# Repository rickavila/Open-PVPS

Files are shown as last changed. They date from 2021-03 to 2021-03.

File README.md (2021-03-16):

# Open-PVPS
Open Source Pandemic Virus Protection Systems

PVPS1 3 6-CADImage

Our goal is to develop open source pandemic virus protection technology that will significantly improve the safety of healthcare workers on the front lines of COVID-19.

To achieve this we are working to substantially reduce the manufacturing and operating cost of a PAPR (https://en.wikipedia.org/wiki/Powered_air-purifying_respirator) while maintaining HEPA filter efficiency (99.97% for 3um particles) with a design that can be easily mass produced anywhere in the world using standard commercial manufacturing machinery and automation. All work performed on this project is open source and freely available with a permissive open source license (CC BY-SA 4.0).

This repository contains a directory for "technical reports", a directory for CAD designs, and a directory for the electronics components. 

The technical reports directory contains documents that describe the technical work, calculations, and decisions that have been made for each major PAPR technical area. The major technical areas are:
* Overall PAPR System Specifications and Performance
* Face Shield, Visor, and Drape (coming soon)
* Power and Control Box
* Blower, Gauge, and Diffuser
* Filter

The CAD directory contains CAD files used to deveop the first PVPS prototypes. The file format is Autodesk Fusion 360. In the future we will also post STL files for anyone that would like to print out the 3D printed components.

The electronics directory contains files that define the physical circuit boards for the battery box and the program for the control board microprocessor. All of the electronics were designed by Jim Hannas with inputs from the team.

This project has a website at http://open-pvps.org

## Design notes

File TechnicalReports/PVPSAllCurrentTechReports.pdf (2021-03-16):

Tech note PVPS - S0001: – System Specifications and Perf | Author: Rick Avila : March 16, 2021

Pandemic Virus Protection Systems

1 | P a g e

Introduction

Similar to other professions involving hazardous environments, healthcare workers who come into contact with COVID-19 patients need equipment that provides high levels of airborne virus protection. Most healthcare institutions that treat COVID-19 patients use disposable N95 masks and plastic face shields which

(1) Do not fully protect the head and neck of the healthcare worker.
(2) Leave marks and bruises due to tight fitting straps around face and ears.
(3) Can be improperly worn without a tight seal.
(4) Can be difficult to breathe through after hours of use.
(5) Are expensive to replace every day for every healthcare worker.

A potential good solution to this problem is to provide each healthcare worker with a Powered Air-Purifying Respirator (PAPR). (https://en.wikipedia.org/wiki/Powered_air-purifying_respirator) However, the cost of commercially available PAPRs is extremely high ($1K to $2K/unit) and the availability is insufficient to support the estimated 18 million healthcare workers in the United States alone. What is needed is a safe and effective PAPR design that can be rapidly mass produced anywhere in the world with standard manufacturing equipment and can be made for as low a cost as possible.

This document outlines the high-level goals, specific technical specifications, and measured performance of the PVPS PAPR.

High Level Goals

- Safety
- Positive pressure keeps virus away from staff
- Quality replaceable air filter (HEPA) keeps breathing air clean
- Check for filter life with simple flow meter (Like commercial PAPR machines)
- Battery indicator allow staff to assure continuous blower function
- (New) Air exiting the PAPR must be filtered to prevent transmission from an infected healthcare worker using the device.
- Visibility
- Large replaceable visor for full viewing visibility
- Clear hood allows safety without isolation
- Comfort and Mobility
- Unit should be easy to wear while working for many hours
- Face shield provides easy doffing and donning
- No long hoses to keep track of
- Wide shroud makes it possible to operate stethoscope

Tech note PVPS - S0001: – System Specifications and Perf | Author: Rick Avila : March 16, 2021

Pandemic Virus Protection Systems

- Disinfection
- Throw away plastic curtain to facilitate easy cleanup
- Simple shape plastic shroud can be cleaned easily with spray and wipes
- Inside of shroud can be cleaned from one person to another easily
- Financial
- Cost must be < $400 for a new unit
- Operating cost must be less than the cost of using disposable respirators (N95 masks) and face shields.

Technical Specifications

- Airflow through filter and blower must be >= 6.0 CFM (169.9 L/min)
- Weight of entire unit must be < 40 ounces (1,133.98 grams)
- Noise level inside face shield must be <= 50 dBA
- Battery life with continuous use must be >= 6 hours
- Battery status must indicate amount of battery remaining
- HEPA filter replacement time must be >= 3 months
- Assigned Protection Factor must be >= 1,000
- Unit must operate for more than 2 years in a healthcare setting

Performance

We have conducted several performance evaluation tests including quantitative tests and healthcare provider evaluations. This section will be updated soon with the results of these tests.

Tech note PVPS - S0001: – System Specifications and Perf | Author: Rick Avila : March 16, 2021

Pandemic Virus Protection Systems

Revision History
Revision | Date | Who | Description
0 | 3/16/2021 | Rick Avila | Creation

Tech note PVPS - B0001: – Blower selection and Design Author: Bob Senzig : Sept 22 2020

Pandemic Virus Protection Systems

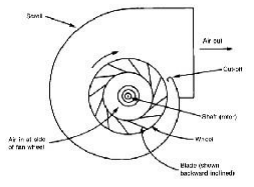
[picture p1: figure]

Blower Background

All commercial PAPR systems utilize a blower as part of the design. Blowers are capable of high flow and deliver a higher-pressure differential than a conventional fan. Our goal is to deliver between 3 and 10 CFM with good output pressure. On the drawing on the right you can see that this type of blower pulls from the inlet and discharge is a 90degree discharge using a centrifugal impeller

Blower Selection

Our final selection is shown here with an attached diffuser/deflector. It is a Foxconn 90mm Blower designed for small form factor Dell computers. It has the right CFM and adequate pressure output and is lightweight. It is a PVB120G12H-P01 J50GH-A00 J50GH 0J50GH 12V 0.75 4Wire Compatible for DELL OptiPlex 790 390 990 SFF CPU Fan Cooling
Fan. It is 146grams.
Initially we evaluated a 70mm blower but it did not provide the

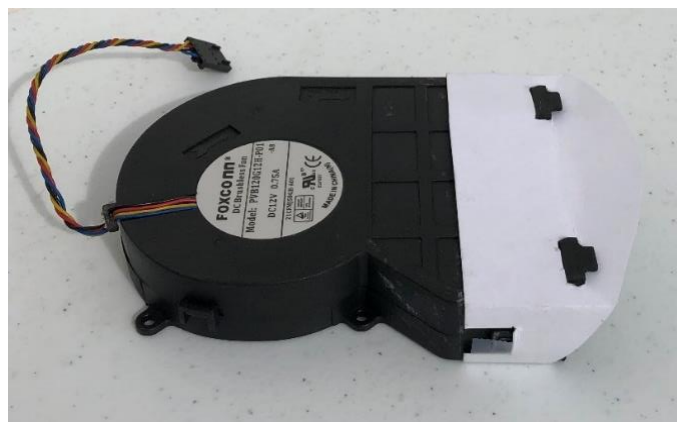
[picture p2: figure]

needed flow with our selected filter. The CFM for blowers are rated with no filter and it drops significantly when the filter is added to the inlet. For example: the GDStime blower is rated at 38CFM but we only saw 11 CFM at 12 volts with the Miller filter. We jumped to a GDSTIME 120mm blower to guarantee enough output. At the time we were using a Miller meter, that drastically underestimated the flow, to determine flow rate. Once we built a full prototype and experienced the impact of weight, we re-evaluated the priority on weight and moved to the smaller and lighter Foxconn 90mm blower. With a calibrated flow measurement, we were able to determine that perhaps a smaller fan could be used. The GDStime blower is 232grams.

Initial testing

Once a prototype was assembled using the 90mm Foxconn blower and Miller filter we conducted some stress tests wearing the mask. These tests were intended to see how the CO2
levels were maintained when doing a strenuous activity. These are not
substitutes for a more clinical environment test but were intended to
give an early indication of any issues. The CO2 levels in the front of the mask were periodically monitored using a Using a CO2 ppm meter periodically during the activity. it was determined that the airflow needed to be focused toward the front of the mask to reduce the CO2

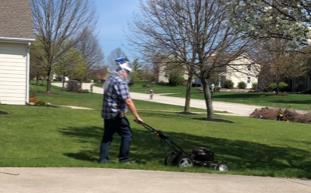
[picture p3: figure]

levels during exertion. A small Diffuser/Defector attached to the output of the blower improved airflow to the front of the mask and reduced the CO2 levels.
https://www.ebay.com/itm/Carbon-Dioxide-Meter-CO2-Detector-Indoor-Air-Quality-RH-Meter-0-2000ppm-rateRange/193507135104?hash=item2d0dec8e80:g:GcgAAOSw8L9e30wF (https://www.ebay.com/itm/Carbon-Dioxide-Meter-CO2-Detector-Indoor-Air-Quality-RH-Meter-0-2000ppm-rateRange/193507135104)

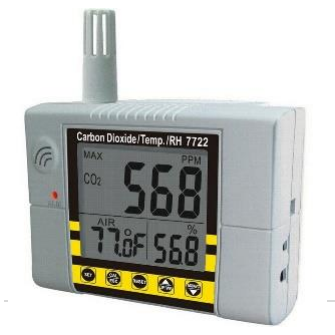
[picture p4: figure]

A finger pulse/O2 meter was not used because prior test showed a long lag and not much sensitivity to the CO2 environment.

Tech note PVPS - B0001: – Blower selection and Design Author: Bob Senzig : Sept 22 2020

Pandemic Virus Protection Systems

Establishing accurate flow

Determining the actual CFM of a given blower was a challenge initially we used a meter form the Miller welding PAPR. There are available for about $10 and initially we though that it would be a good indicator of achieving the required 6CFM flow since that is how it is used. It was eventually determined that the flow was being underestimated by that meter. This was determined using
a stop watch and measuring the time it took to fill a
standard 30 gallon garbage bag. It was determined that

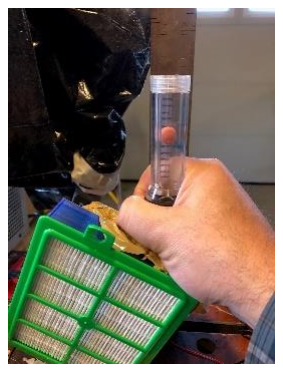
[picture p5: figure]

the Miller meter was not responsive enough to measure the desired flow range 3-10 CFM. Using the stop watch and bag method the flow rate was accurately determined. The volume of the bag was determined by this estimation method and using the height and width of the uninflated bag.

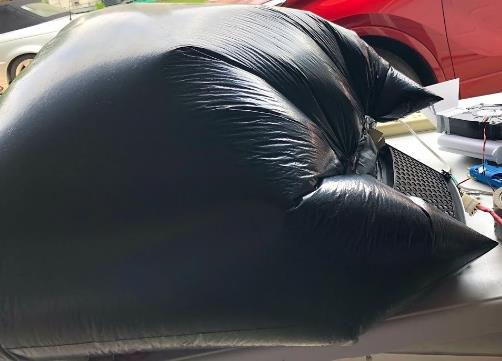
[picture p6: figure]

https://en.wikipedia.org/wiki/Paper_bag_problem.

Meter refinement

Obviously, It is not convenient to use a bag for all tests. This Sensirion SFM3000 Flow meter was utilized. It was calibrated against the bag flow estimation and the Miller meter. With these measurements it is possible for a given blower and filter combination to predict airflow by input voltage and to convert the measurement of the Sensirion flow meter to CFM. This proved very helpful to understand the true
airflow rates.

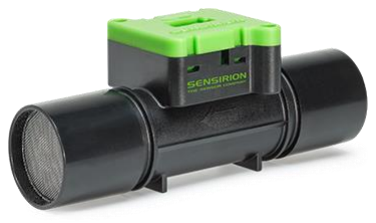
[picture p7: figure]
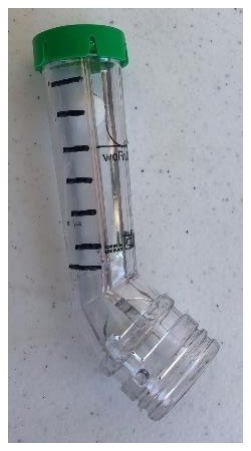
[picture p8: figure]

PAPR regulations require some type of flow QC check to understand the state of the blower and filter. This is the purpose of the Miller meter (left). As stated, we found that the meter was not calibrated for our device and we needed to adjust its sensitivity. The diameter of the ball was measured and the ball 3D printed in a series of different fill factors to find the right weight. The cap of this style meter is easy to remove and reapply so we used this to develop our version of the QC check. A 0.25gram 12.5mm ball was what was needed to measure the 6CFM from our system.

Tech note PVPS - B0001: – Blower selection and Design Author: Bob Senzig : Sept 22 2020

Pandemic Virus Protection Systems

Blower performance

Figure 1:

time to fill (sec) | CFM* | LPM* | SFM3000 | Volts
21.35 | 8.78575 248.7847 | 72 | 12 | 8.8
26.57 | 7.059682 199.9079 | 60 | 10 | 7.1
30.58 | 6.133936 173.6937 | 53.5 | 9 | 6.1
32.17 | 5.830766 165.1089 | 51 | 8.8 | 5.8
32.96 | 5.691012 161.1515 | 50.5 | 8.6 | 5.7
34.7 | 5.405641 153.0707 | 49 | 8.4 | 5.4
35.4 | 5.29875 150.0439 | 46 | 8 | 5.3
61 | 3.075012 87.07465 | 29.5 | 5.9 | 3.1
- From bag testing

Figure 2:

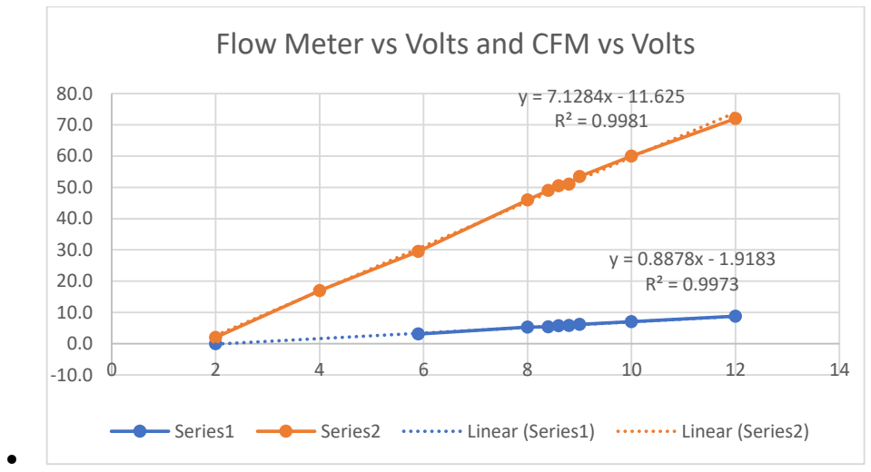
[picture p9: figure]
Flow Meter vs Volts and CFM vs Volts; Series1; Series2; Linear (Series1); Linear (Series2)

With these two charts one can use volts to estimate the CFM on a system with a fresh filter or use these two equations to solve for the CFM as a function of SFM300 meter reading on any condition system.

First equation from curve fit says:

SFM3000=7.1284*Volts – 11.625 So:

Volts=(SFM3000+11.625)/7.1284

Second equation from curve fit is:

CFM=(0.8878*Volts-1.9183) – [Convert Volts to CFM for a clean filter]

Substituting. you get….

CFM=(0.8878*((SFM300+11.625)/7.1284))-1.9183 – [Convert SFM300 measurement to CFM for any condition filter and Foxconn blower]

CFM estimate from
equation and
Sensirion
measurement

Tech note PVPS - B0001: – Blower selection and Design Author: Bob Senzig : Sept 22 2020

Pandemic Virus Protection Systems

Other considerations:

The PVP-D(Backpack) concept has to use a hose to connect to the Face Shield/Hood. There is considerable loss in the hose. While se intend to mitigate that by using a larger diameter hose it seems that the pressure drop will make the Foxconn less desirable in this configuration.

Conclusion:

The Foxconn blower can deliver up to 8.8CFM with a clean filter and is adequate for the job. The GDStime blower may be a better design choice when weight is not as critical and a higher output is needed. The GDStime blower can deliver up to 10.9 CFM at 12.3 volts.

For the PVP-P (top of head) and PVP-B (Back of head) based design where the weight must be carried on the head, it is recommended to use the Foxconn blower. For the PVP-D (backpack) design the GDStime may be a better choice.

Tech note PVPS - B0001: – Blower selection and Design Author: Bob Senzig : Sept 22 2020

Pandemic Virus Protection Systems

Revision History
Revision | Date | Who | Description
0 | 9/22/2020 | Bob Senzig | Creation

Tech note PVPS - F0001: – Filter selection and Design Author: Bob Senzig : Sept 17 2020

Pandemic Virus Protection Systems

Filter Background

An N95 disposable mask is considered an adequate protection for many healthcare workers. An N95 mask blocks 95% of incoming particles if properly fitted. (https://en.wikipedia.org/wiki/N95_mask) This effectiveness is lesser for particles which are smaller than 0.3 microns. This may not be adequate for prolonged exposure or for use in areas where the viral load is high. Our goal is to create a device that offer more complete protection for those
situations. Human breathing has a tidal volume of 0.5 liters 10-20 times a minute.
This means that the human lungs are essentially a 0.35CFM pump. A N95 Filter is

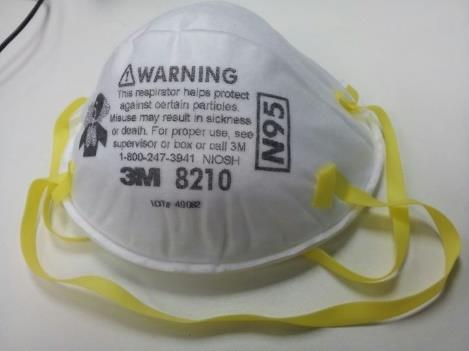
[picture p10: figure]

around 45 IN**2. This yields an air speed of around 0.2 inches/sec. A cough or sneeze is much higher speed but we will focus on steady state breathing. We will try to show that the powered PAPR design can provide much more protection than the N95 for the wearer. A powered PAPR is not a good choice in an environment where the virus load is low because there is not filtration of the exit air. Later in the technote you will be able to see why the N95 mask material cannot be used as is in a powered unit where the airflow is increased.

HEPA filters are rated to remove 99.97% of particles greater than 0.3 micron. (https://en.wikipedia.org/wiki/HEPA) HEPA filter are available in many configuration Vacuum Cleaner, Air Freshener, Auto cabin and commercial PAPR filters. Our focus was to find a practical and economical solution that would me our performance goals.

Filter Selection

Filter selection is key to effective protection. There are two main candidates for the PVP-P device filter:

1. Miller PAPR HE particle filter designed for use in a
Miller T94-R™ Miller welding system (part number
235673). It is a HEPA rated filter and is designated
as NIOSH purple (High Efficiency (HE) Filter, P100 Filters).
2. Freudenberg unreleased proto PAPR filter. This a filter designed by Freudenberg Filtration Technologies a leader in automotive, industrial and environmental filters for use in a PAPR. We were able to obtain prototype units for evaluation.
We deprioritized this filter due to availability
beyond the evaluation units.

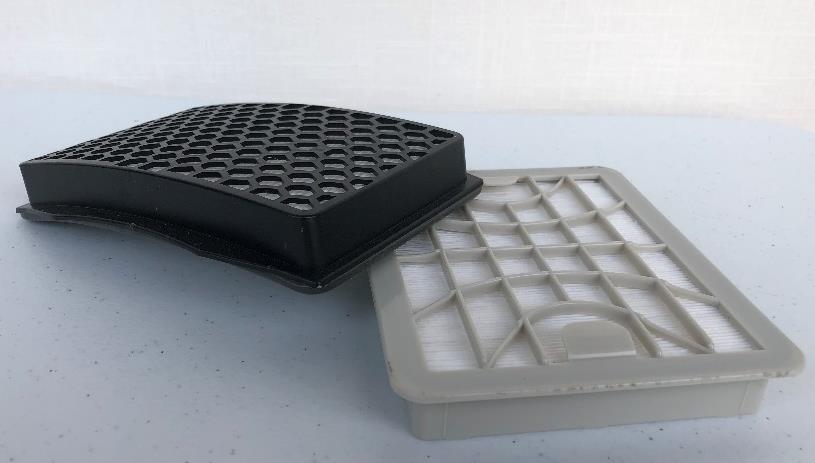
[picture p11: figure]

3. Holmes air freshener filter provide a similar size but larger True HEPA filter that can be adapted to this use. We have deprioritized this filter due to the larger size and weight concerns.

Filter evaluation criteria were simple, a size and weight compatible with our head top PVP-P and backpack style PVP-D concepts, a back pressure compatible with the blower choice, excellent filtration capability, easily handles and replaced.

1. Filtration must provide adequate filtration at the max flow rate the PAPR is capable of
2. Size: must be less than ??? x?? x ??? and less than ??? grams to be considered
3. Back pressure must provide low resistance so that lightweight blowers can deliver the required minimum 6CFM and a higher flow rate of at least 9CFM

Tech note PVPS - F0001: – Filter selection and Design Author: Bob Senzig : Sept 17 2020

Pandemic Virus Protection Systems

4. Easy to handle we felt that filters with a plastic carrier were easier to install and remove than the automotive style cartridge felt filters
1) Filter Design

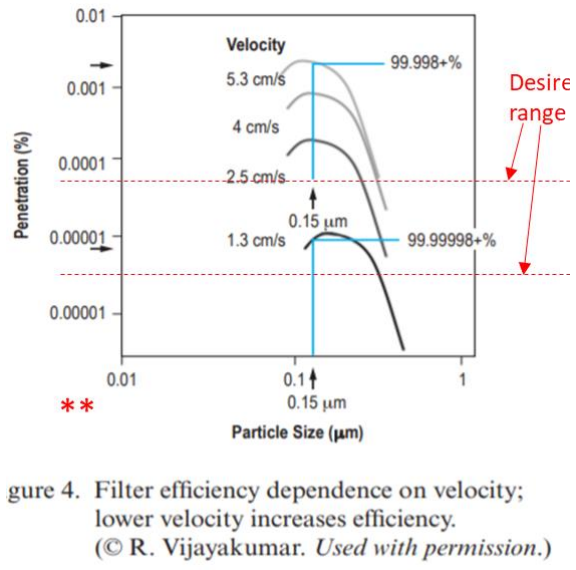
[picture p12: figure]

Not being an expert in filter design we did some searching and found some useful information

a. Impact of air speed on filter efficiency

The NASA paper Submicron and Nanoparticulate Matter Removal by HEPA-Rated Media Filters and Packed Beds of Granular Materials- (https://ntrs.nasa.gov/archive/nasa/casi.ntrs.nasa.gov/20170005166.pdf) Perry et al shows the relationship of air speed and filtration in Figure 4. I added the red color annotation to show the range we want to operate in for the best filtration performance.

b. HEPA filter efficiency for COVID-19 sized particles

Filtration of airborne microorganisms: Modeling and prediction – 1999 Kowalski et al (https://www.semanticscholar.org/paper/Filtration-of-airborne-microorganisms%3A-Modeling-and-Kowalski-Bahnfleth/f1106423c4ff158e85d99db783669fb6a31ca5a9?p2df) provides info on HEPA filter performance with different size particles. Here the size of the COVID particle is added for clarity. So even though the rating for a HEPA filter is a 0.3microns it does very well on COVID-19 sized particles. In Figure 9 from that publication shows the performance with Coronavirus size particles

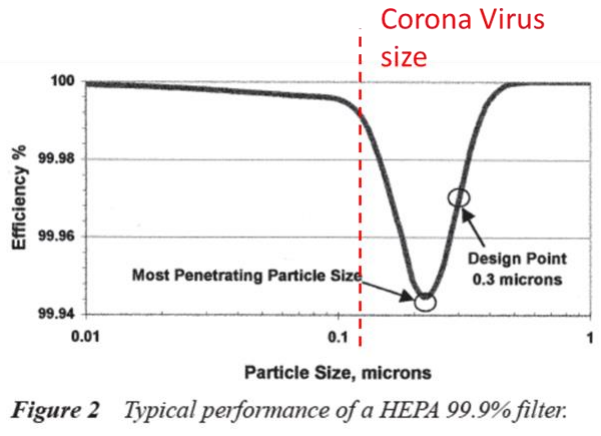
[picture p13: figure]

Tech note PVPS - F0001: – Filter selection and Design Author: Bob Senzig : Sept 17 2020

Pandemic Virus Protection Systems

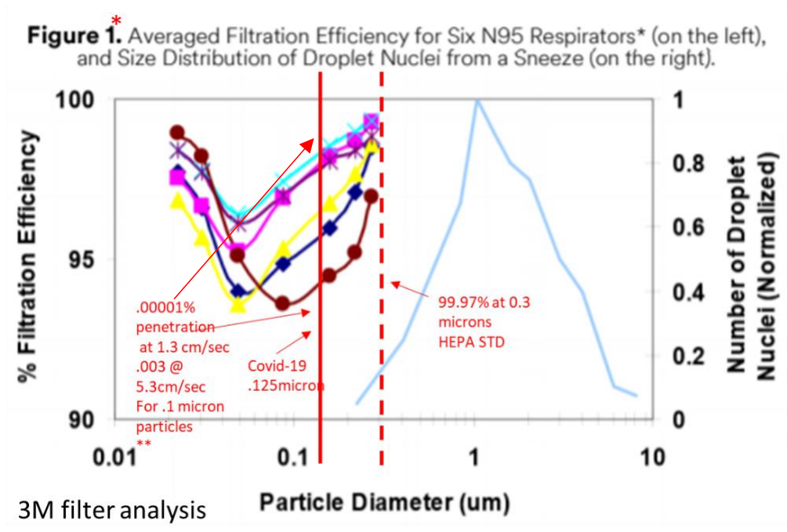
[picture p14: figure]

This figure from a 3M analysis of how N95 masks performs against a water droplet (cough) and Covid-19 sized particles shows that even having an airspeed higher than 5.3 cm/sec the HEPA filter yields superior performancehttps://fastlifehacks.com/n95-vs-ffp/ (https://fastlifehacks.com/n95-vs-ffp/)

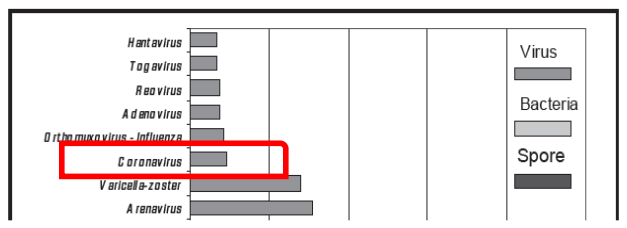
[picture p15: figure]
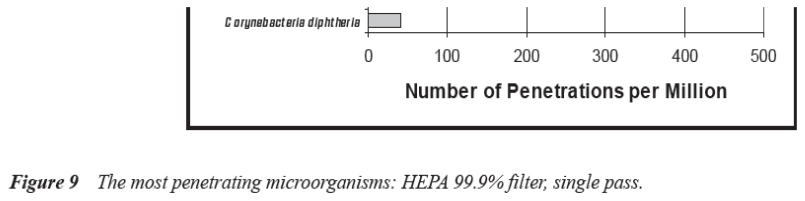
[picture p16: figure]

Tech note PVPS - F0001: – Filter selection and Design Author: Bob Senzig : Sept 17 2020

Pandemic Virus Protection Systems

In this figure the impact of speed on pressure drop is shown. To get a reasonable pressure drop so the blower does not have to work as hard a low air speed is desired. I added the scale to make interpretation easier. This is from Recent advances in antimicrobial air filter – Komaladewi et al (https://www.researchgate.net/publication/329188177_Recent_advances_in_antimicrobial_air_filter)

2) Filter Physical Size

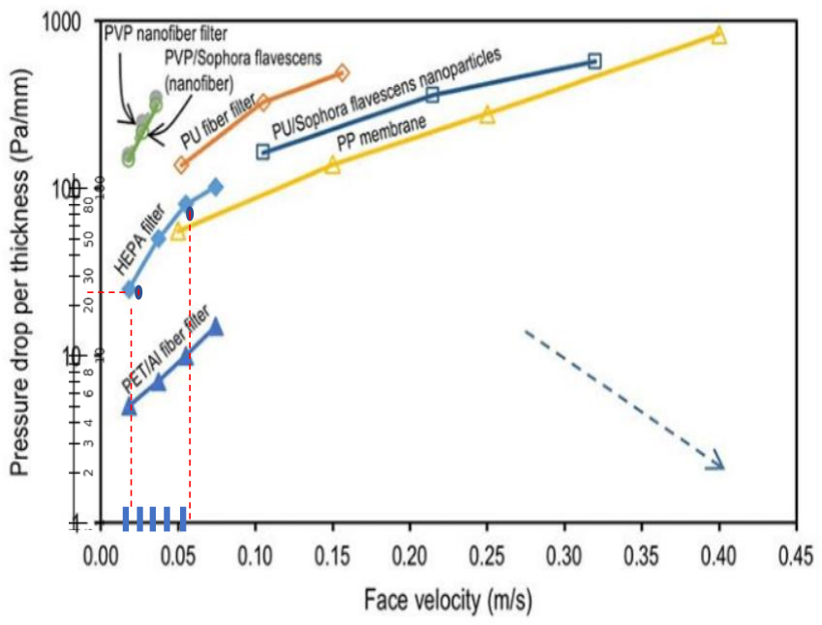
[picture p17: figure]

The Face Shield/Hood structure in the PVP-P concept and the mini backpack desired in the PVP-D design limit the practical filter size to 5 x 10” inches. For PVP-P a
smaller 7x4” is more desirable. Filter size to achieve
the desired air speed you can calculate the needed
filter square area from the CFM flow rate and the desired speed. It is not possible to meet the size constraints with a single layer filter. A pleated filer design is required. This equation was described in a design notes created by Arron Sun on the OPEN PAPR Facebook site. (https://aaronsun.com/projects/emergency-medical-devices/powered-respirator/flow-calculations) The following table shows 3 different available filters that we down selected and the anticipated filter performance,

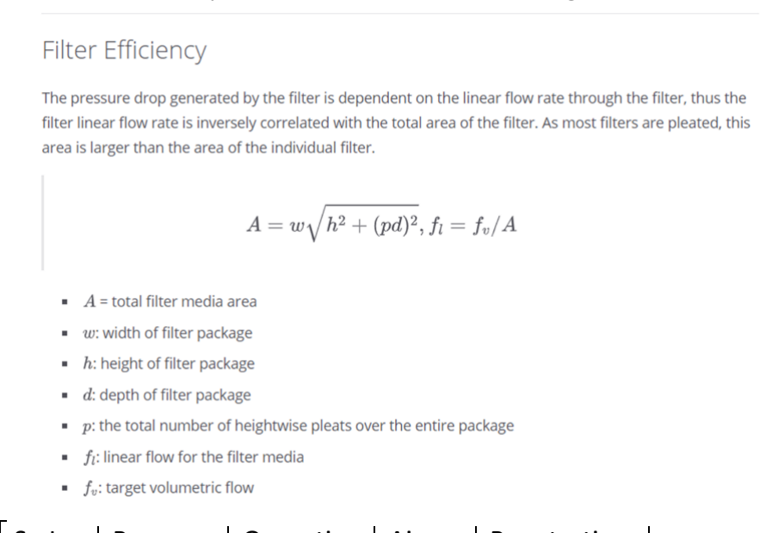
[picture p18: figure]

Filter | Height | Width | thickness | #Folds | Sq In filter area | Pressure drop @6CFM | Operating CFM | Air Speed in/sec | Penetration %
Freudenberg | 6.3 | 4.8 | .86 | 51 | 458 | Med | 6 | .376 | 0.000006
Holmes | 9.5 | 4.1 | 1.13 | 53 | 418 | Low | 6 | .414 | 0.00001
Miller | 6.5 | 3.75 | .5 | 65 | 224 | High | 6 | 1.026 | 0.00016
N95 | 7 | 7 | N/A | N/A | 49 | N/A | 0.35 | .201 | 5%

From this analysis, the packaging and the availability criteria, the Miller filter was chosen as the primary filter. We also considered that this particular filter would not be in high demand for healthcare use because of the weight and design of the commercial Miller welding PAPR, the unit is not practical in a healthcare environment. We thought that this would likely mean filters would stay readily available.

Tech note PVPS - F0001: – Filter selection and Design Author: Bob Senzig : Sept 17 2020

Pandemic Virus Protection Systems

Revision History
Revision | Date | Who | Description
0 | 9/22/2020 | Bob Senzig | Creation

Tech note PVPS - F0001: – Filter selection and Design Author: Bob Senzig : Sept 17 2020

Pandemic Virus Protection Systems

3) Ease of filter change/Packaging

Tech note PVPS - F0001: – Filter selection and Design Author: Bob Senzig : Sept 17 2020

Pandemic Virus Protection Systems

This 3M publication presents performance of a N95 mask vs particle size. Technical Data Bulletin #174 Respiratory Protection for Airborne Exposures to Biohazards (https://multimedia.3m.com/mws/media/409903O/respiratory-protection-against-biohazards.pdf)

Comparison between Prototype and proposed Control specifications 2020-05-05

Electronic Control specifications (preliminary)

1. Will use an off-shelf M18 battery (Milwaukee Electric Tool or other brands compatible with MET chargers)
2. Will provide a single pushbutton which will cycle from OFF to a number of fan speeds yet to be determined.
3. Will monitor Battery voltage and Fan amperage to determine the following conditions:
a. Low Battery (verified by using the battery indicator build into the battery pack
b. Possible Filter sealing issues or blockage.
4. Will begin modulating the fan between the selected speed and the maximum speed to indicate any of the fault conditions listed above.
5. Will remove power to the Fan connector within 5 seconds after the Fan is disconnected.
6. Will remove power to the Fan connector when the battery voltage drops below 14.5 volts.
7. Will be sealed to allow outer-surface cleaning

Five Prototype Manual Control boxes - 2020-05-04

- The only user control is a potentiometer which allows adjustment of the output voltage between two internal trim pot values. The initial minimum is set at 7.85v which has been determined by filter testing with a GDStime GDB1232Q2005 Blower.
- They provide crude battery discharge protection at >13.5 volts, where the minimum specified limit is 12.7 volts before battery damage starts to occur.
- The battery protection will cut power to the fan. However, the estimated run time from even the smallest available MET pack is close to 10 hours.
- These prototypes provide no user feedback for low battery or filter problems.
- These prototypes are NOT sealed and should only be wiped down with alcohol to remove contaminants.

Propellerhead PAPR Hood - Electronics Design Diary

2020-05-05 - Preliminary Electronic Control specifications
1. Will use an off-shelf M18 battery (Milwaukee Electric Tool or other brands compatible with MET chargers)
2. Will provide a single pushbutton which will cycle from OFF to a number of fan speeds yet to be determined.
3. Will monitor Battery voltage and Fan amperage to determine the following conditions:
a. Low Battery (verified by using the battery indicator build into the battery pack
b. Possible Filter sealing issues or blockage.
4. Will begin modulating the fan between the selected speed and the maximum speed to indicate any of the fault conditions listed above.
5. Will remove power to the Fan connector within 5 seconds after the Fan is disconnected.
6. Will remove power to the Fan connector when the battery voltage drops below 14.5 volts.
7. Will be sealed to allow outer-surface cleaning

2020-05-04 - Qty 5 Proto Battery Boxes have been assembled

- The only user control is a potentiometer which allows adjustment of the output voltage between two internal trim pots. The initial minimum is set at 7.85v which has been determined by filter testing with a GDStime GDB1232Q2005 Blower.
- They do provide crude battery discharge protection below 13.5 volts, where the minimum specified limit is 12.7 volts before battery damage stats to occur.
- The battery protection will cut power to the fan. However, the run time from even the smallest available MET pack is close to 10 hours.
- These prototypes provide no user feedback for low battery or filter problems.
- These prototypes are NOT sealed and should only be wiped down with alcohol to remove contaminants.
- Each box took 13 Hours to print. Each cover took 1 Hour to print.

2020-04-22 - First Proto Battery Box given to Bob for testing
2020-04-14 - First printing of MET adapter version 13
Due to the time-consuming measurements required to provide a usable interface, it took a lot longer than I thought to model the battery adapter in SCAD. This box will be used to make the first prototype control with a potentiometer.

2020-04-08 - Design Constraints
At this point there are more PCB mechanical concerns than there are electrical concerns. Since a circuit design is highly dependent on resolving these issues, I will try to list the issues to see if we can keep this project on track.

Propellerhead PAPR Hood - Electronics Design Diary

1. Location of the PCB - The major issue with electronics is disinfection. Even if the PCB is conformal-coated, physical stresses during wipe down could cause component damage, ESD could cause electrical damage and chemicals could damage connectors.
a. If the PCB is in the Hood then it will be subjected to the user-generated pathogens and will need to be cleaned occasionally.
b. If the PCB is in the Blower Backpack, the user controls would have to the remotely located.
c. If the PCB is in the Battery Assembly it would not require any cleaning. Even with both designs mechanical buttons through small holes in the case would be accessible. An Overlay would be inexpensive and provide a durable seal. With the proper material selection, overlay chemical cleaning would not be an issue. The number of connections is reduced because the battery wires would tie into the PCB
2. Wiring between components. With normal use, wires will break over time, connectors will get dirty, break or may disconnect unless secured.
a. Connector to Battery Pack. Details are available. Durability may be an issue. One person suggested using epoxy to secure the pins and wires to the 3D printed assembly. This is time consuming in production. An injection-molded part with inserted pins exceeds the project time budget.
b. Cable between Battery connector and Battery Assembly Output connector. This should include a 1/2 Amp replaceable fuse.
c. Cable between Battery Assembly and Hood or Backpack Assembly. This should have connectors on both ends to allow replacement if damage occurs. There should also be a means to firmly secure it to the Battery Assembly.

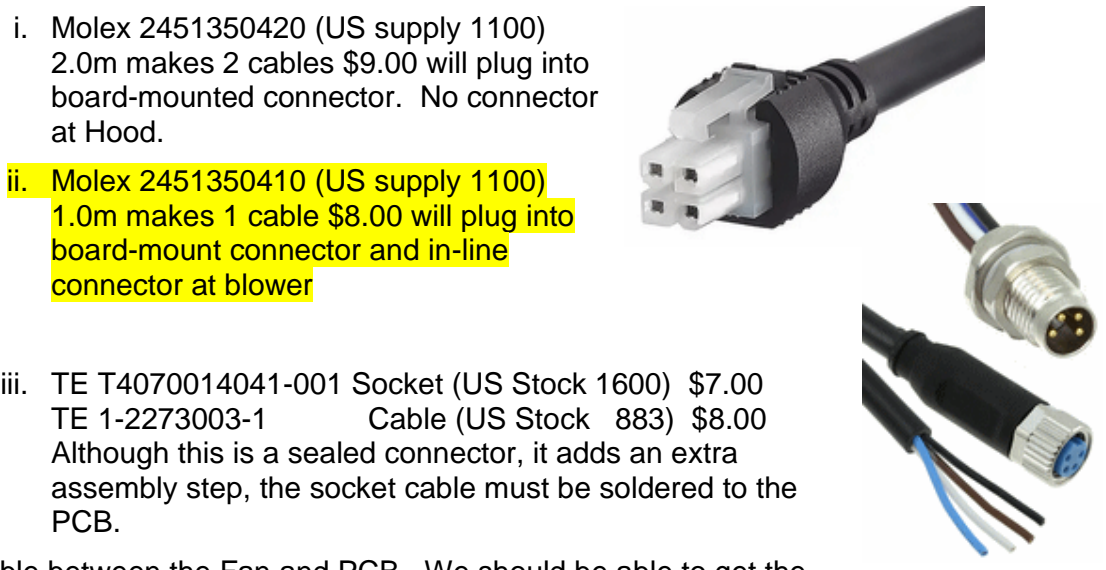
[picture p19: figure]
at Hood.; ii. Molex 2451350410 (US supply 1100) 1.0m makes 1 cable $8.00 will plug into board-mount connector and in-line connector at blower; PCB.

i. Molex 2451350420 (US supply 1100)
2.0m makes 2 cables $9.00 will plug into
board-mounted connector. No connector

iii. TE T4070014041-001 Socket (US Stock 1600) $7.00
TE 1-2273003-1 | Cable (US Stock 883) $8.00
Although this is a sealed connector, it adds an extra assembly step, the socket cable must be soldered to the
d. Cable between the Fan and PCB. We should be able to get the
Fan with a connector. This would plug into a socket on the PCB.
e. Cable between the PCB and Buttons. Unless the buttons can be mounted on the PCB (preferred) a cable will be required.

Propellerhead PAPR Hood - Electronics Design Diary

i. Although Capacitive touch would eliminate a number of cleaning issues, research indicates that reliability and noise immunity may not make this approach practical. The time development and testing time would exceed the project time budget.
ii. Medical Graphic Overlay with 2 buttons requires some tooling, but would be able to be placed on the top of the hood. The hole in the hood would be covered by the label and the adhesive would provide a durable seal. Include in the assembly is an integral flex cable with connector that plugs into the PCB. The length of this cable is limited.
iii. Mechanical buttons on PCB that would protrude through holes in the top of the mask. An Overlay would be inexpensive and provide a durable seal. With the proper material selection, cleaning would not be an issue.
iv. If the PCB is located in a blower backpack, a cable and button assembly would be required. Depending on where this would be mounted, durability and disinfection will be issues.
f. System Feedback - Devices include LEDs, Vibrators and Beepers.
i. LEDs require a remotely-located circuit board within range of the user’s vision, cable and connectors. It will be subjected to cleaning. Or have to be in a housing. Lots of design compromises.
ii. A Vibrator in the Battery Assembly might not be felt through all of the clothing that the user wears.
iii. A Beeper requires a physical opening to produce a high sound level
1. If it is located in the Battery Assembly it will be exposed to room
pathogens and possibly allow disease transmission.
2. For the PropellerHead, it could be located in the exit of the Blower. A third wire would be needed in the cable to the PCB in the Battery Assembly.
3. For the Blower Backpack, it could be located behind the Filter. The sound should be able to exit through the filter.
3. MTBF - is directly related to how many parts are involved in a system. Keeping the number of parts to a minimum ensures better reliability over time.
4. Time to Production - With each component in the system there is time to research availability, engineer the component, design the tooling, produce the tooling, procure materials and setup production lines. Our time is very limited. We must concentrate on the best way to build this product with the least number of manufacturing steps.

2020-04-07 - Switch to MET 4.0Ah and 5.0Ah batteries
I spent the morning dissecting my Milwaukee Electric Tool M18 components, a Drill, a charger and two battery packs that are still in production.
I also went to Home Depot and looked at other brands. None of the others appeared to be any better. Since my packs used Samsung cells, I researched their available cells and discovered a good correlation between the different MET packs and the cells.
Analysis: PAPR_Battery_comparison.doc

Propellerhead PAPR Hood - Electronics Design Diary

2020-04-06 - Blowers Arrived
They seem to draw 1/2 the current that was specified on Alibaba. Not sure they will have the capacity we require. If they do, we will require only 4 watts.

2020-04-03 - Placed Digikey order $209.22

2020-04-07 Update - This order is useless because we changed Batteries. Will attempt to return the 2 - ADM00865 MCP1665 Switcher Demo Kits $86.00

2020-04-02 -

2020-04-01 - Possible Conflicts After our evening discussion,

2020-03-31 - Possible Conflicts
I wish we had a year to develop all of the features that you proposed. There are so many unknowns and conflicts in this project that some features might not be possible in the time we have..
My initial concept is to use Fan Motor Amperage for battery and filter status.
- Depending on the resolution of this monitor circuit, we might be able to get an idea of the filter status, but it may not be possible with the three fan speeds, unknown sealing and variations in filter density.
- The difference between the absence or presence of a filter will make a big difference in the fan amperage. However, the change between a clean filter and a clogged filter may be so miniscule that it may not be detectable except at the highest fan speed and a known throat sealing situation. The throat seal will probably introduce far more variation in amperage than a clogged filter.
- The least expensive CO2 module appears to be around $40. But, the effectiveness of such a monitor is highly dependent on where it is placed in the hood, will be subject to deterioration due to the high moisture content in the hood..
- We made the decision to go to Off-Shelf Phone Charger battery packs to allow for better availability. However, no two packs will have similar capacities. This is in direct conflict with the battery Life monitoring because we will not know the total battery capacity. We can ASSUME, but will not have control of what happens in the field. Field adjustment of battery life would not be possible unless the facility always used the exact same packs for every mask. Most hospitals have a person that verifies equipment and performs minor maintenance. Therefore, we might have to grossly under-estimate the capacity.

USB Support
- I have to talk with Darryl to see if he has ever done an integrated USB, but at this time, rolling USB support into the single Micro of this project does not appear to provide any benefit that justifies the time (which would include a PC Driver and programming user interface). This is

Propellerhead PAPR Hood - Electronics Design Diary

why many development boards have a separate Micro dedicated to the USB programming port.
- Many of the projects that I have worked on over the past 20 years are setup with the ability to initially program the Micro using a connector-less connection to the manufacturer's standard programmers as well as re-programming and monitoring of run-time parameters with an inexpensive serial interface.
- The alternative is to do what has been done on development boards. Add a USB interface chip which could be removed from the production board. The cost of these devices includes the Driver support and allows serial re-programming and monitoring of run-time parameters. LED and buttons with the dinosaur approach
- Once the Fan moves out of the helmet onto a backpack, buttons and LEDs become very difficult.
- There are a few possible solutions
- Use a 10 conductor cable that travels up the inside (or outside) of the airway between the circuit board by the motor/battery to the LED/button board.
- Use a 4 conductor cable to travels up the inside (or outside) of the airway between the circuit board by the motor to a separate micro on the LED/button board.
- Eliminate the LED/button board and use the audible alarm to indicate battery and filter status by a series of short tones with pauses that decrease as battery life decreases. Someone else would have to control the fan.
- (Bob) If we have a necklace to hold the bottom to a shape could the buttons and indicator be added to that? What do you recommend?
- Wireless would require a separate battery on the LED/button which would require additional maintenance.

Propellerhead PAPR Hood - Electronics Design Diary

2020-03-27 - Control Board initial refinements
Controls and indicators
Two Switches, On/Off (Left) and Fan Speed (Right)
- Pressing On/Off will toggle On-Off
- Pressing Fan Speed will loop through available speeds
- Pressing both buttons for 2 seconds will reset Battery Life Timer LEDs
- 4 total, 2 Green, 2 Red-Green
- 2 Green and 1 Red-Green will make up a Battery Life bar
- 3 Green - 100% Battery
- 2 Green - 75% Battery
- 1 Green - 50% Battery
- 1 Yellow - (Red+Grn) 25% Battery
- 1 Red Flashing - 10% Battery
- 1 for possible Filter Status, Green-OK, Yellow-Clog, Red-No Filter??

Propellerhead PAPR Hood - Electronics Design Diary

2020-03-26 - Preliminary Control Board Requirements

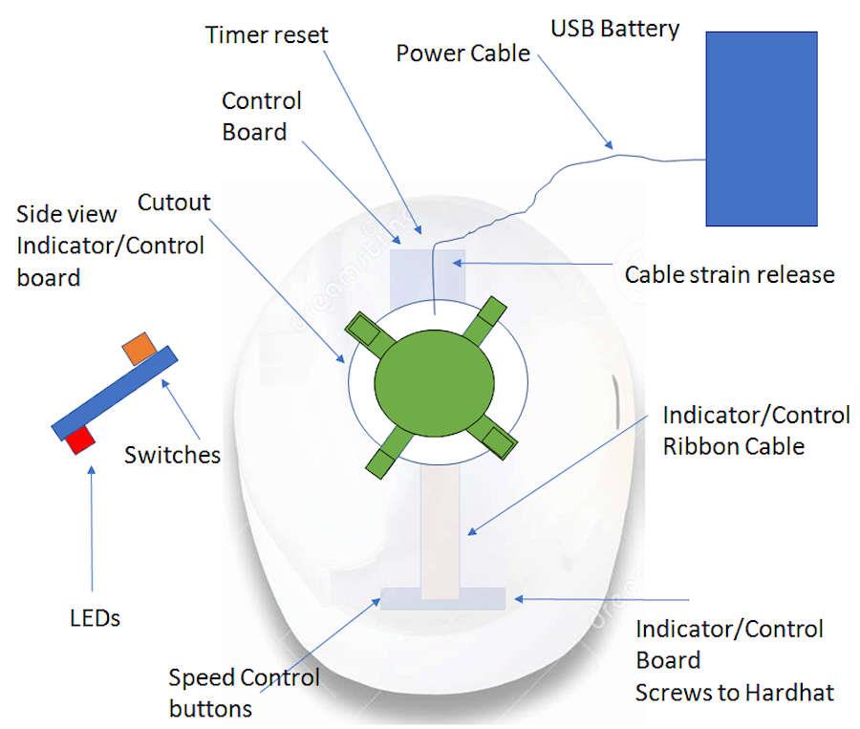
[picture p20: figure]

1. Fan Speed – External access
- Goal: Maintain positive pressure at all speeds. User can set required speed
- Solution :
- 4 Speeds –
- Minimum Speed still needs to pressurize bag,
- Medium speed – Set for conversation level,
- Max speed based on Max tolerated noise
- Momentary Ludicrous speed – Fan Max for bag flushing and seal test at bag installation
- Momentary off – For stethoscope listening, and inaudible conversation
- Standby Off – two quick presses of momentary off will sound an audible and visual indicator that the system will shut off in 10 seconds. If the button is pressed once again the standby off is abandoned. The timer shall be suspended if the 10seconds are complete and standby Off is activated

Propellerhead PAPR Hood - Electronics Design Diary

2. Battery life
- Goal: Provide the wearer and support staff an indicator of battery life of standard USB batteries
- Solution: To utilize standard USB batteries with no feedback the battery life is tracked via amperage over time
- A means shall be proved to reset the timer when a fresh battery is installed
- An internal button provided so that when a fresh battery is installed and the fan starts the timer starts
- The timer reset button can be activated with a heavy magnet placed on the timer activation sensor. With this a user can reset the timer if they install a fresh battery
- When the battery timer reaches 75% of the expected life a yellow LED is activated
- 3 Green LED will track the progress of the Battery timer
- When the Timer reaches 90% of the expected life a RED blinking LED is activated and an audible alarm sounds
- Audible Alarms need to be audible inside the helmet
- Visual alarms need to be visible to the wearer and the person servicing the battery
- Battery status can blink slowly to conserve battery power
- Selected Fan speed will be considered when tracking battery time on
- Expected battery life should be 13 hours
3. Filter indicators
- Goal: Provide feedback on properly installed filter and clogged filter
- Solution: Use motor speed amperage as an indication of back pressure
- If too little resistance in detected a Filter installation error alarm and indicator are activated
- If too much resistance is detected the filter clogged error alarm and indicator are activated
- Since these levels are unknown the design limits shall be settable via the USB cable.

2020-03-25 - Blowers Ordered - $37.05

An order was placed through Alibaba with Susan from xinyujie.com.

2020-03-22 - And so it begins

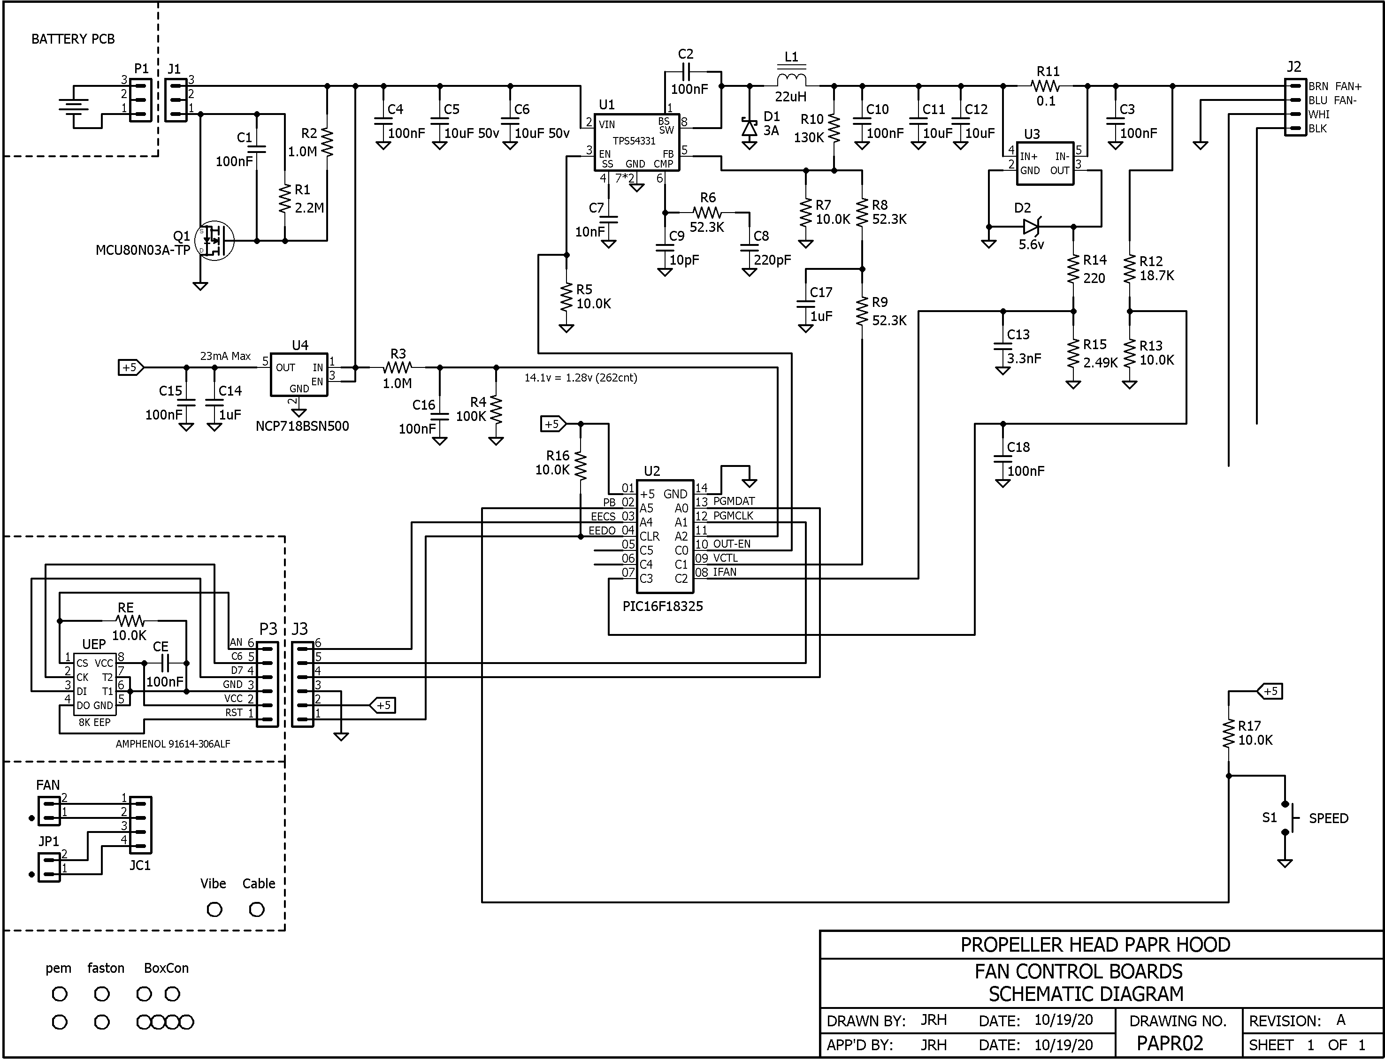
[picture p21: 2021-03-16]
Electronics/PAPR_02__schematic.png

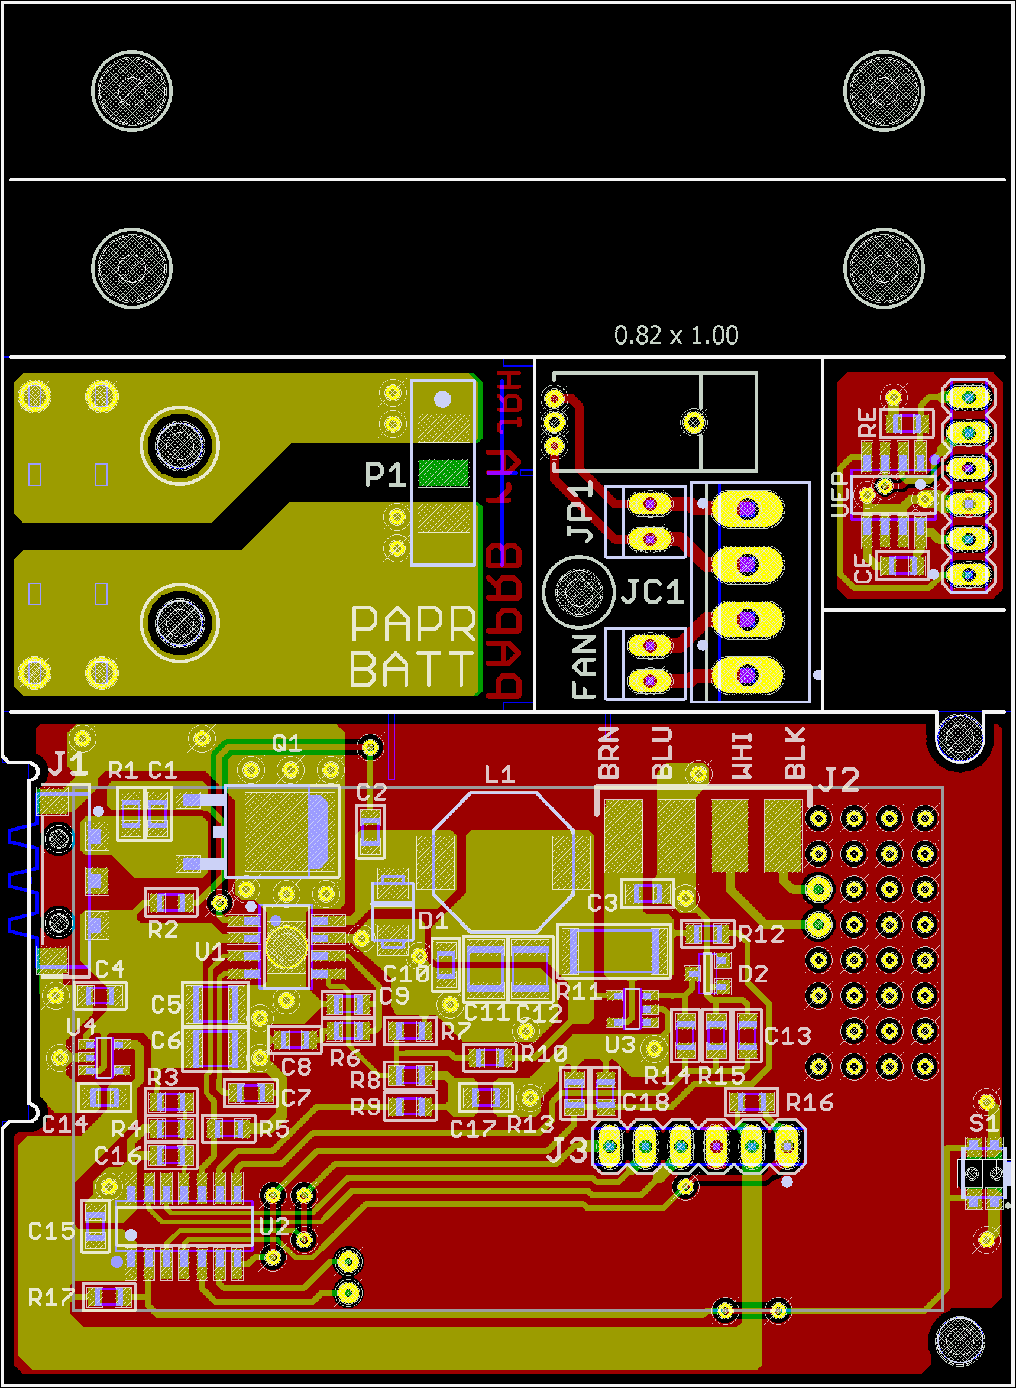
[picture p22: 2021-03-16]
Electronics/PAPR_02__layout_color.png

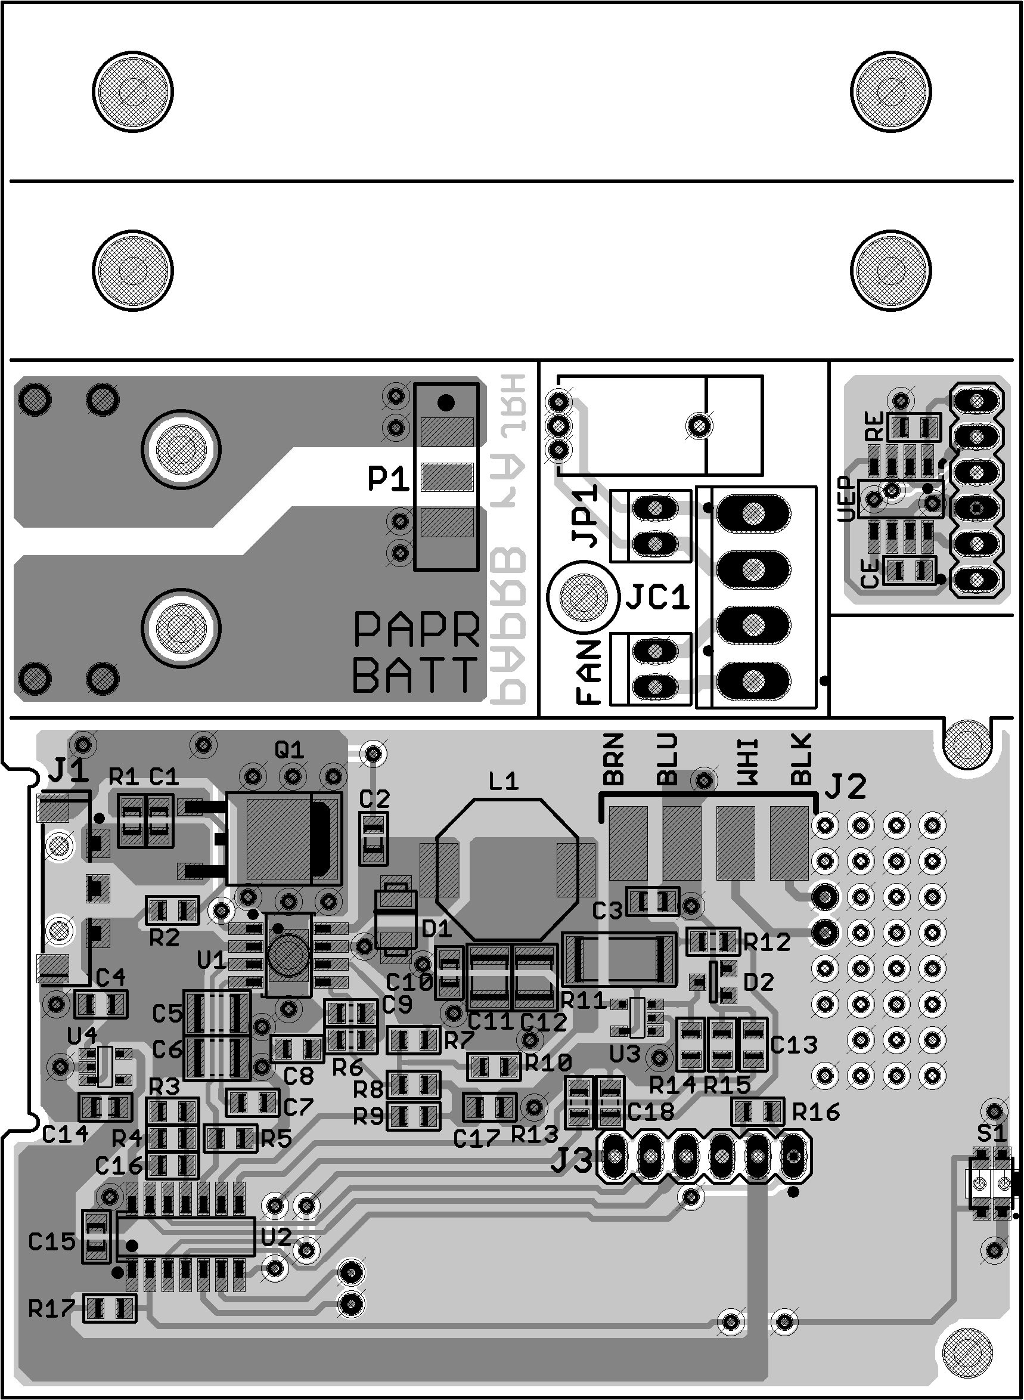
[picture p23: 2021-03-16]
Electronics/PAPR_02__layout_bw.png

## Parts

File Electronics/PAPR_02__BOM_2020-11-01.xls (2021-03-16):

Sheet: Sheet1
Item | Qty | Description | Mfg | Mfg Part Number | Designators | Package | Possible Supplier | Reel Size | Cost Qty | Price
1 | 1 | Capacitor,10pF,50v, MonoCer,NPO,10% | Kemet Stackpole | C0805C100K5GACTU CML0805C0G100JT50V | C9 | R0805 | Digikey 399-7975-1-ND |  | 10 | 0.0810
2 | 1 | Capacitor,220pF,50v, MonoCer,NPO,5% | Samsung Kemet | CL21C221JBANNNC C0805C0G500-221JNE | C8 | R0805 | Digikey 1276-1164-1-ND |  | 10 | 0.0510
3 | 1 | Capacitor,3.3nF,50v, MonoCer,X7R,10% | Kemet | C0805C332K5RACTU | C13 | R0805 | Digikey 399-1153-1-ND |  | 10 | 0.0640
4 | 1 | Capacitor,10nF,50v, MonoCer,X7R,10% | Samsung AVX | CL21B103KBANNNC C0805C103K1RAC7210 | C7 | R0805 | Digikey 1276-1015-1-ND |  | 10 | 0.0520
5 | 9 | Capacitor,100nF,50v, MonoCer,X7R,10% | Samsung AVX | CL21B104KBC5PNL 08055C104KAT4A | C1-C4,C10, C15-C16,C18,CE | R0805 | Digikey 1276-7000-1-ND 478-10836-1-ND |  | 100 | 0.0317
6 | 2 | Capacitor,1uF,50v, MonoCer,X7R,10% | Samsung Taiyo Yuden | CL21B105KOFNNNG EMK212B7105KG-T | C14,C17 | R0805 | Digikey 1276-6471-1-ND |  | 10 | 0.0630
7 | 2 | Capacitor,10uF,50v, MonoCer,X7R,10% | TDK | C3225X7R1H106M250AC | C5-C6 | R1210 | Digikey 445-14933-1-ND |  | 10 | 0.8220
8 | 2 | Capacitor,10uF,25v, MonoCer,X7R,10% | Samsung Taiyo Yuden | CL32A106KAULNNE TMK325BJ106KN-T | C11,C12 | R1210 | Digikey 1276-1854-1-ND 587-5950-1-ND |  | 100 | 0.1386
9 | 1 | Diode,3A,40V,Schottky,SMA | Diodes Inc OnSemi Vishay | B340A-13-F MBRA340T3G SSA34HE3_A/I | D1 | SMA | Digikey B340A-FDICT-ND MBRA340T3GOSCT-ND SSA34HE3_A/IGICT-ND |  | 10 | 0.3320
10 | 1 | Zener,5.6v,250mW,SOT23-3 | On Semi | SZBZX84-C5V6LT1G | D2 | SOT23-3 | Digikey SZBZX84C5V6LT1GOSCT-ND |  | 10 | 0.1290
11 | 1 | Header,3 pin, 3.2mmcc Leaf Spring | TI | 1745142-1 | J1 | 1746142 | Digikey A107932CT-ND |  | 10 | 1.6470
12 | 1 | Header,4p,SMD,MicroMate 3mm c-c | TE | 2-1445091-4 | J2 | 2-1445091-4 | Digikey A123007CT-ND |  | 10 | 1.2050
13 | 1 | Header,6p,thru,gold,8.89mm | Samtec | MTSW-106-22-G-S-350 | J3 | J06P | Digikey MTSW-106-22-G-S-350-ND |  | 1 | 0.7500
14 | 1 | Inductor,uH,10mm Octal | Bourns | SDR1048-220Y | L1 | SRU1048 | Digikey SRU1048-220YCT-ND |  | 10 | 0.9340
15 | 1 | MOSFET,N-Ch,30v,<18m | MCC Diodes Inc On Semi | MCU80N03A-TP DMG4800LK3-13 NTD4969NT4G | Q1 | TO252 | Digikey 353-MCU80N03A-TPCT-ND |  | 10 | 0.4000
16 | 1 | Resistor,220,1/8w,1% | Stackpole KOA Speer | RMCF0805FT220R RK73H2ATTD2200F | R14 | R0805 | Digikey RMCF0805FT220RCT-ND |  | 100 | 0.0104
17 | 1 | Resistor,2.49K,1/8w,1% | Stackpole Vishay | RMCF0805FT2K49 CRCW08052K49FKEA | R15 | R0805 | Digikey RMCF0805FT2K49CT-ND |  | 100 | 0.0104
18 | 6 | Resistor,10.0K,1/8w,1% | Stackpole KOA Speer | RMCF0805FT10K0 RK73H2ATTD1002F | R5,R7,R13, R16,R17,RE | R0805 | Digikey RMCF0805FT10K0CT-ND |  | 100 | 0.0104
19 | 1 | Resistor,18.7K,1/8w,1% | Stackpole Yageo | RMCF0805FT18K7 RC0805FR0718K7L | R12 | R0805 | Digikey RMCF0805FT18K7CT-ND |  | 100 | 0.0104
20 | 3 | Resistor,52.3K,1/8w,1% | Yageo Vishay | RC0805FR-0752K3L CRCW080552K3FKEA | R6,R8,R9 | R0805 | Digikey 311-52.3KCRCT-ND |  | 100 | 0.0163
21 | 1 | Resistor,100K,1/8w,1% | Stackpole KOA Speer | RMCF0805FG100K RK73H2ATTD1003F | R4 | R0805 | Digikey RMCF0805FT100KCT-ND |  | 100 | 0.0104
22 | 1 | Resistor,130K,1/8w,1% | KOA Speer Yageo | RK73H2ATTD1303F RC0805FR-07130KL | R10 | R0805 | Digikey 2019-RK73H2ATTD1303FCT-ND |  | 100 | 0.0136
23 | 2 | Resistor,1.0M,1/8w,1% | Stackpole KOA Speer | RMCF0805FG1M00 RK73H2ATTD1004F | R2,R3 | R0805 | Digikey RMCF0805FG1M00CT-ND 2019-RK73H2ATTD1004FCT-ND |  | 100 | 0.0104
24 | 1 | Resistor,2.2M,1/8w,1% | Stackpole Vishay | RMCF0805FT2M21 CRCW08052M20FKEA | R1 | R0805 | Digikey RMCF0805FT2M21CT-ND |  | 100 | 0.0143
25 | 1 | Resistor,0.1,2w,1% | Stackpole | CSRN2512FTR100 | R11 | R2512 | Digikey CSRN2512FTR100CT-ND |  | 10 | 0.4620
26 | 1 | PushButton,Low Profile,Rt Angle | Panasonic | EVQ-P7C01P EVQ-P7A01P | S1 | EVQ-P7C01P | Digikey P16763CT-ND P16765CT-ND (Prefered) |  | 10 | 0.2870
27 | 1 | Switching Regulator,3A,25v | TI | TPS54331DDAR | U1 | SO08PW | Digikey 296-39419-1-ND |  | 10 | 1.3520
28 | 1 | Microcontroller,8bit,14pin | Microchip | PIC16F18325-I/SL | U2 | SOIC14 | Digikey PIC16F18325-I/SL-ND |  | 1 | 0.9800
29 | 1 | Hi-Side Amps Monitor | DiodesInc | ZXCT1010E5TA | U3 | SOT23-5 | Digikey ZXCT1010CT-ND |  | 10 | 1.0250
30 | 1 | Regulator,LoQ,5.0v,25vIn | On Semi | NCP718BSN500T1G | U4 | SOT23-5 | Digikey NCP718BSN500T1GOSCT-ND |  | 10 | 0.3380
31 | 0 | Serial EEPROM, 8K | ROHM Semi | BR93H76RFJ-2CE | UEP | SO08 | Digikey BR93H76RFJ-2CE2CT-ND |  | 25 | 0.4130
32 | 1 | Circuit Board |  |  |  |  |  |  | 10 | 15.0000
 | 50
70 | 2 | PEM Fastener | PEM Engineering | KF2-440-ET | BOM1,BOM2 |  | ??? |  | 10 | 0.4000
72 | 0 | Vibrator | Jinlong | Z6SCAB0061141 | BOM5 |  | Digikey 1670-1021-ND |  | 1 | 2.8800
73 | 1 | Connector,Circular,4p | TE | T4070014041-001 | BOM6 |  | Digikey A126812-ND |  | 10 | 7.6590
74 | 1 | Cable,Circular,4p | TE | 1-2273003-1 | BOM7 |  | Digikey A120949-ND |  | 10 | 10.7000
75 | 1 | Plug,4p,MicroMate 3mm c-c | TE | 1445022-4 | BOM8 |  | Digikey A30260-ND |  | 10 | 0.4040
76 | 4 | Terminal,male, MicroMate, gold,30u | TE | 1-794606-1 |  |  | Digikey A100439CT-ND |  | 50 | 0.1086
71 | 2 | Terminal, Faston 0.250 | Keystone | 4901 | BOM3,BOM4 |  | Digikey 36-4901-ND |  | 10 | 0.2296

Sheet: Sheet2
Qty | Digikey Part Number | Price | Description
15 | 399-7975-1-ND | 0.0810 | Capacitor,10pF,50v, MonoCer,NPO,10%
15 | 1276-1260-1-ND | 0.0510 | Capacitor,3.3nF,50v, MonoCer,X7R,10%
15 | 1276-1015-1-ND | 0.0520 | Capacitor,10nF,50v, MonoCer,X7R,10%
135 | 1276-7000-1-ND | 0.0317 | Capacitor,100nF,50v, MonoCer,X7R,10%
15 | 1276-6471-1-ND | 0.0630 | Capacitor,1uF,50v, MonoCer,X7R,10%
30 | 445-14933-1-ND | 0.8220 | Capacitor,10uF,50v, MonoCer,X7R,10%
100 | 1276-1854-1-ND | 0.1386 | Capacitor,10uF,25v, MonoCer,X7R,10%
15 | B340A-FDICT-ND | 0.3320 | Diode,3A,40V,Schottky,SMA
15 | SZBZX84C5V6LT1GOSCT-ND | 0.1290 | Zener,5.6v,250mW,SOT23-3
15 | A107932CT-ND | 1.6470 | Header,3 pin, 3.2mmcc Leaf Spring
15 | A123007CT-ND | 1.2050 | Header,4p,SMD,MicroMate 3mm c-c
15 | MTSW-106-22-G-S-350-ND | 0.7500 | Header,6p,thru,gold,8.89mm
15 | SRU1048-220YCT-ND | 0.9340 | Inductor,uH,10mm Octal
15 | 353-MCU80N03A-TPCT-ND | 0.4000 | MOSFET,N-Ch,30v,<18m
100 | RMCF0805FT220RCT-ND | 0.0104 | Resistor,220,1/8w,1%
100 | RMCF0805FT2K49CT-ND | 0.0104 | Resistor,2.49K,1/8w,1%
100 | RMCF0805FT10K0CT-ND | 0.0104 | Resistor,10.0K,1/8w,1%
100 | RMCF0805FT18K7CT-ND | 0.0104 | Resistor,18.7K,1/8w,1%
100 | 311-52.3KCRCT-ND | 0.0163 | Resistor,52.3K,1/8w,1%
100 | RMCF0805FT100KCT-ND | 0.0104 | Resistor,100K,1/8w,1%
100 | 2019-RK73H2ATTD1303FCT-ND | 0.0136 | Resistor,130K,1/8w,1%
100 | RMCF0805FG1M00CT-ND | 0.0104 | Resistor,1.0M,1/8w,1%
100 | RMCF0805FT2M21CT-ND | 0.0143 | Resistor,2.2M,1/8w,1%
15 | CSRN2512FTR100CT-ND | 0.4620 | Resistor,0.1,2w,1%
15 | P16763CT-ND | 0.2870 | PushButton,Low Profile,Rt Angle
15 | 296-39419-1-ND | 1.3500 | Switching Regulator,3A,25v
15 | PIC16F18325-I/SL-ND | 0.9820 | Microcontroller,8bit,14pin
15 | ZXCT1010CT-ND | 1.0250 | Hi-Side Amps Monitor
15 | NCP718BSN500T1GOSCT-ND | 0.3380 | Regulator,LoQ,5.0v,25vIn
1 | 1670-1021-ND | 0.2880 | Vibrator
15 | A126812-ND | 7.6590 | Connector,Circular,4p
15 | A120949-ND | 10.7000 | Cable,Circular,4p
15 | A30260-ND | 0.4040 | Plug,4p,MicroMate 3mm c-c
60 | A100439CT-ND | 0.1086 | Terminal,male,MicroMate, Ag,30u
30 | 36-4901-ND | 0.2296 | Terminal, Faston 0.250

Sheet: Sheet3
15 | 399-7975-1-ND
15 | 1276-1260-1-ND
15 | 1276-1015-1-ND
135 | 1276-7000-1-ND
15 | 1276-6471-1-ND
30 | 445-14933-1-ND
100 | 1276-1854-1-ND
15 | B340A-FDICT-ND
15 | SZBZX84C5V6LT1GOSCT-ND
15 | A107932CT-ND
15 | A123007CT-ND
15 | MTSW-106-22-G-S-350-ND
15 | SRU1048-220YCT-ND
15 | 353-MCU80N03A-TPCT-ND
100 | RMCF0805FT220RCT-ND
100 | RMCF0805FT2K49CT-ND
100 | RMCF0805FT10K0CT-ND
100 | RMCF0805FT18K7CT-ND
100 | 311-52.3KCRCT-ND
100 | RMCF0805FT100KCT-ND
100 | 2019-RK73H2ATTD1303FCT-ND
100 | RMCF0805FG1M00CT-ND
100 | RMCF0805FT2M21CT-ND
15 | CSRN2512FTR100CT-ND
15 | P16763CT-ND
15 | 296-39419-1-ND
15 | PIC16F18325-I/SL-ND
15 | ZXCT1010CT-ND
15 | NCP718BSN500T1GOSCT-ND
1 | 1670-1021-ND
15 | A126812-ND
15 | A120949-ND
15 | A30260-ND
60 | A100439CT-ND
30 | 36-4901-ND

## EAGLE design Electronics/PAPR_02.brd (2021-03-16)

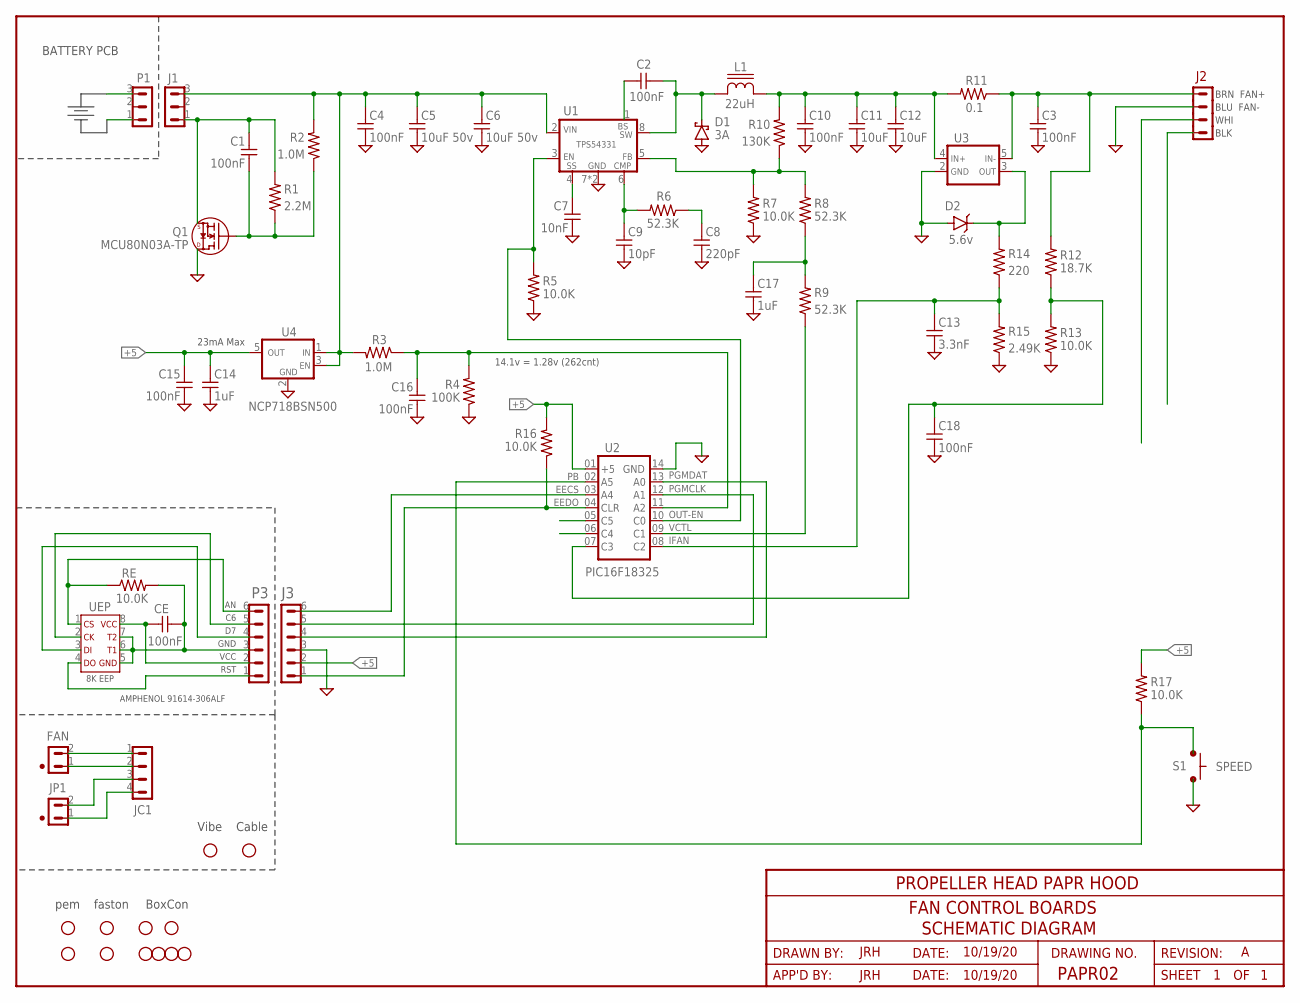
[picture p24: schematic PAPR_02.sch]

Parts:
BOM1, BOM2: pem; BOM_ADDER; PART_NUMBER KF2-440-ET
BOM3, BOM4: faston; BOM_ADDER; PART_NUMBER 4901
BOM5: vibrator; BOM_ADDER; PART_NUMBER Z6SCAB0061141
BOM6: BoxCon; BOM_ADDER; PART_NUMBER T4070014041-001
BOM7: Cable; BOM_ADDER; PART_NUMBER 1-2273003-1
BOM8: Plug; BOM_ADDER; PART_NUMBER 1445022-4
BOM9, BOM10, BOM11, BOM12: Pin; BOM_ADDER; PART_NUMBER 1-794606-1
C1, C2, C3, C4, C10, C15, C16, C18: 100nF; R0805; PART_NUMBER CL21B104KBC5PNL 08055C104KAT4A
C5, C6: 10uF 50v; R1210; PART_NUMBER C3225X7R1H106M250AC
C7: 10nF; R0805; PART_NUMBER CL21B103KBANNNC C0805C103K1RAC7210
C8: 220pF; R0805; PART_NUMBER CL21C221JBANNNC C0805C0G500-221JNE
C9: 10pF; R0805; PART_NUMBER C0805C100K5GACTU CML0805C0G100JT50V
C11, C12: 10uF; R1210; PART_NUMBER CL32A106KAULNNE TMK325BJ106KN-T
C13: 3.3nF; R0805; PART_NUMBER C0805C332K5RACTU
C14, C17: 1uF; R0805; PART_NUMBER CL21B105KOFNNNG EMK212B7105KG-T
CE: 100nF; R0805; PART_NUMBER CL21B104KBC5PNL 08055C104KAT4A
D1: 3A; SMA; PART_NUMBER B340A-13-F MBRA340T3G SSA34HE3_A/I
D2: 5.6v; SOT23-3; PART_NUMBER SZBZX84-C5V6LT1G
FAN: Fan_Hdr; 641215-2
J1: bat; 1746142
J2-BLK, J2-BLU, J2-BRN, J2-WHI: WIRE-HDRS200; PADS200
J3: 6p; J06P; PART_NUMBER MTSW-106-22-G-S-350
JC1: Cable_Termination; B4P-VH
JP1: Spare; 641215-2
L1: 22uH; SRU1048
P1: bat; 1746142M
P3: 6p plug; J06P
Q1: MCU80N03A-TP; TO252; PART_NUMBER MCU80N03A-TP DMG4800LK3-13 NTD4969NT4G
R1: 2.2M; R0805; PART_NUMBER RMCF0805FT2M21 CRCW08052M20FKEA
R2: 1.0M; R0805; PART_NUMBER RMCF0805FG1M00 RK73H2ATTD1004F
R3: 1.0M; R0805; PART_NUMBER RMCF0805FT2M21 CRCW08052M20FKEA
R4: 100K; R0805; PART_NUMBER RMCF0805FG100K RK73H2ATTD1003F
R5, R7, R13, R16, R17: 10.0K; R0805; PART_NUMBER RMCF0805FT10K0 RK73H2ATTD1002F
R6, R8, R9: 52.3K; R0805; PART_NUMBER RC0805FR-0752K3L CRCW080552K3FKEA
R10: 130K; R0805; PART_NUMBER RK73H2ATTD1303F RC0805FR-07130KL
R11: 0.1; R2512; PART_NUMBER CSRN2512FTR100
R12: 18.7K; R0805; PART_NUMBER RMCF0805FT18K7 RC0805FR0718K7L
R14: 220; R0805; PART_NUMBER RMCF0805FT220R RK73H2ATTD2200F
R15: 2.49K; R0805; PART_NUMBER RMCF0805FT2K49 CRCW08052K49FKEA
RE: 10.0K; R0805; PART_NUMBER RMCF0805FT10K0 RK73H2ATTD1002F
S1: SPEED; EVQ-P7C01P
U1: TPS54331; SO08PW
U2: PIC16F18325; SOIC14; PART_NUMBER PIC16F18325-I/SL
U3: ZXCT1010; SOT23-5
U4: NCP718BSN500; SOT23-5; PART_NUMBER NCP718BSN500T1G
UEP: 4K EEP; SO08; PART_NUMBER BR93H76RFJ-2CE

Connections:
+5: C14.1, C15.1, J3.2, R16.1, R17.1, U2.01 (VCC), U4.5 (OUT)
BAT+: C4.1, C5.1, C6.1, J1.3, R2.1, R3.1, U1.2 (VIN), U4.1 (IN), U4.3 (EN)
BAT-: C1.1, J1.1, Q1.2 (S), R1.1
BATT+: P1.3
BATT-: P1.1
BOOST: C2.1, U1.1 (BS)
CMP: C9.1, R6.1, U1.6 (CMP)
ECK: P3.5, UEP.2 (SK)
ECS: P3.6, RE.2, UEP.1 (CS)
EDI: P3.4, UEP.3 (DI)
EDO: P3.1, UEP.4 (DO)
EECS: J3.6, U2.03 (A4)
EEDO: J3.1, R16.2, U2.04 (CLR)
EGND: CE.2, P3.3, RE.1, UEP.5 (GND), UEP.6 (T1), UEP.7 (T2)
FB: R7.1, R8.1, R10.2, U1.5 (FB)
GND: C3.2, C4.2, C5.2, C6.2, C7.2, C8.2, C9.2, C10.2, C11.2, C12.2, C13.2, C14.2, C15.2, C16.2, C17.2, C18.2, D1.A, D2.1 (A), J2-BLU.1, J3.3, Q1.3 (D), R4.2, R5.2, R7.2, R13.2, R15.2, S1.1, S1.2 (1), U1.7 (GND), U1.9 (GND), U2.14 (GND), U3.2 (GND), U4.2 (GND)
IFAN: C13.1, R14.2, R15.1, U2.08 (C2)
J2-3: J2-WHI.1
J2-4: J2-BLK.1
unnamed: C1.2, Q1.1 (G), R1.2, R2.2
unnamed: CE.1, P3.2, UEP.8 (VCC)
unnamed: C3.1, J2-BRN.1, R11.2, R12.1, U3.5 (IN-)
unnamed: C18.1, R12.2, R13.1, U2.07 (C3)
unnamed: D2.3 (C), R14.1, U3.3 (OUT)
unnamed: C8.1, R6.2
unnamed: FAN.2, JC1.1
unnamed: FAN.1, JC1.2
unnamed: JC1.3, JP1.2
unnamed: JC1.4, JP1.1
OUT+: C10.1, C11.1, C12.1, L1.2, R10.1, R11.1, U3.4 (IN+)
OUT-EN: R5.1, U1.3 (EN), U2.10 (C0)
PB: R17.2, S1.3 (2), S1.4 (2), U2.02 (A5)
PGMCLK: J3.5, U2.12 (A1)
PGMDAT: J3.4, U2.13 (A0)
PWMF: C17.1, R8.2, R9.1
SS: C7.1, U1.4 (SS)
SW: C2.2, D1.C, L1.1, U1.8 (SW)
U2-05: U2.05 (C5)
U2-06: U2.06 (C4)
VBAT: C16.1, R3.2, R4.1, U2.11 (A2)
VCTL: R9.2, U2.09 (C1)

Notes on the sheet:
PROPELLER HEAD PAPR HOOD
FAN CONTROL BOARDS
SCHEMATIC DIAGRAM
PAPR02
JRH
10/19/20
pem
faston
BATTERY PCB
8K EEP
RST
VCC
GND
AMPHENOL 91614-306ALF
BRN FAN+
BLU FAN-
WHI
BLK
23mA Max
14.1v = 1.28v (262cnt)
Vibe
BoxCon
Cable

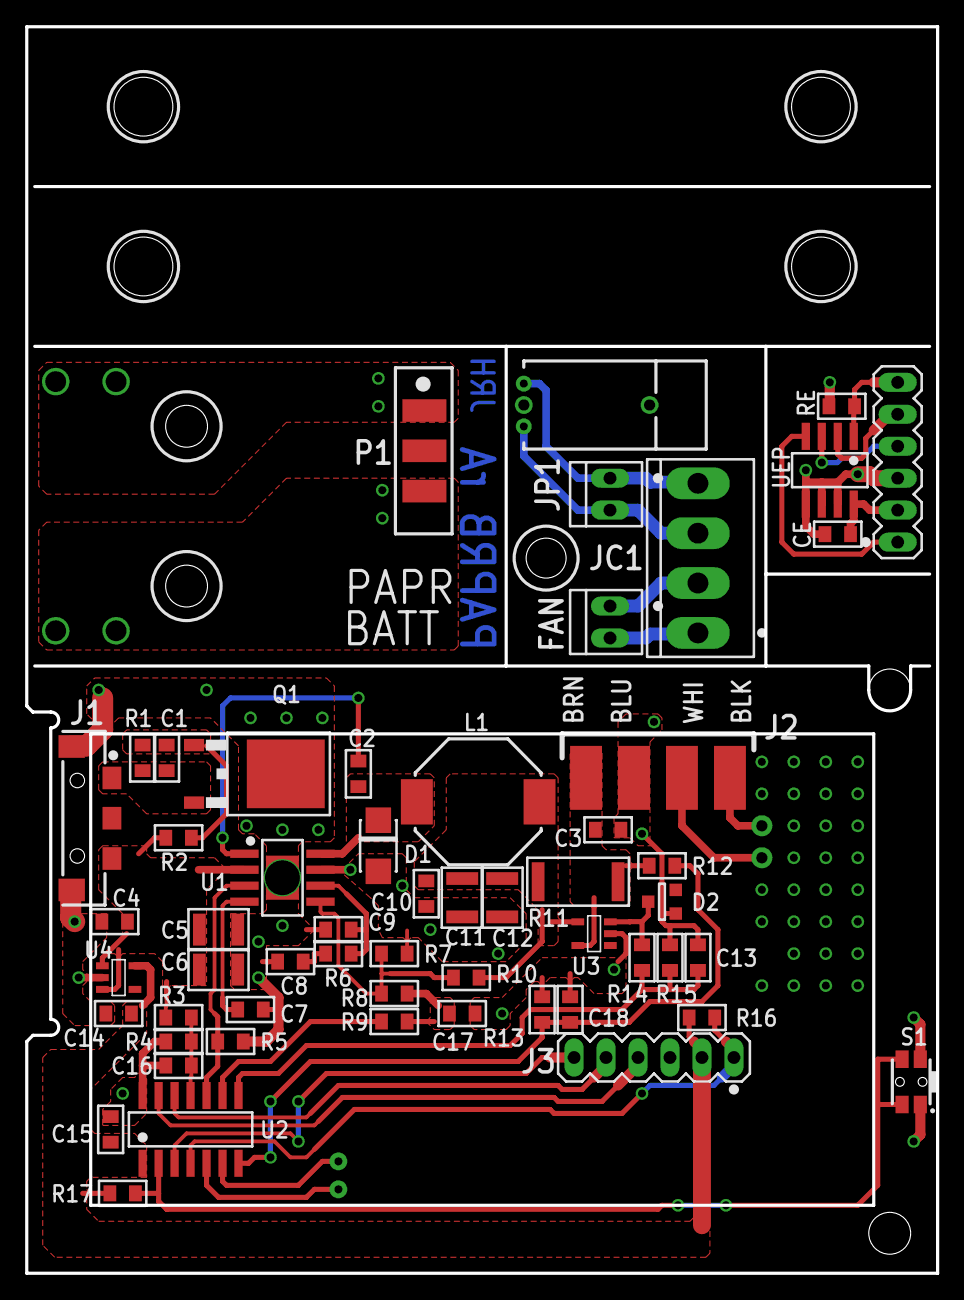
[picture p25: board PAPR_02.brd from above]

Board: 2 copper layers, 72.4 x 99.1 mm, 70 parts (0 on the bottom side), 35 nets.

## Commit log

2020-05-30 Create PVP v 1.3.1 Suspension .f3z
    This Fusion 360 file contains both the PVP1.3.1 face shield and the face shield adapter (holds 3M head gear to face shield).
2020-05-30 Changed the name of the head gear suspension
    because Bob wanted it that way...
2020-10-11 Added the latest PVP CAD design containing all major components.
    [PVPv1.3.6 Slim Ring v8.stl]
2021-03-15 First Technical Notes
    Adding technical notes for blower and filter.
2021-03-16 Added a document that includes all current technical reports.
2021-03-16 Electronics files provided by Jim Hannas
    [PAPR_02.brd, PAPR_02.sch, PAPR_02__BOM_2020-11-01.xls]
2021-03-29 PVP 1.3.6 All Parts with Slim Filter Adapter Design
    [PVPv1.3.6 Slim Ring v8.stl]
